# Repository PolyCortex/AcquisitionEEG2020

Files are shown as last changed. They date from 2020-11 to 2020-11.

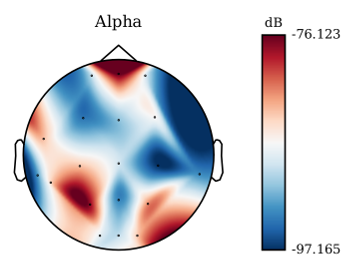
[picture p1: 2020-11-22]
software/gui/img/mne_head.png

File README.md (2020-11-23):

<h1 align="center">
  <br>
  Acquisition board 2020
  <br>
  Acquisition board 2020
  <br>
</h1>

<h4 align="center">A 4-channels biosignal acquisition pipeline.</h4>
<p align="center">
  <a href="http://polycortex.polymtl.ca/">
    
  </a>
 </p>

<p align="center">
  <a href="#key-features">Key Features</a> •
  <a href="#how-it-works">How It Works</a> •
  <a href="#project-structure">Project Structure</a> •
  <a href="#learn-more">Learn more</a> •
  <a href="#learn-more">About us</a>
</p>

---

The project contained in this repository is a 4-channel prototype board produced in the development of a PCB to acquire EEG signals. It contains an instrumentation amplifier, a notch filter and an anti aliasing filter. It is designed to be sampled either in a lab with the help of an oscilloscope or with a computer through a Teensy 3.2 microcontroller development board. As well, a signal visualization software can analyze the signal coming from this board.

**Disclaimer:** This prototype board does not work to sample EEG signals and was never intended as such. It was meant to be a platform used to test designs of filtering and amplification circuits, which we would have integrated into a true production PCB. However, our development cycle was slowed down due to the pandemic and we had to plan the release of the production version of the board for April 2021 instead. Even though we did not finish the project, we still wanted to show our progress and so we submit this prototype for the NeuroTechX 2020 Fixed Challenge.

## Key features

- A PCB which amplifies the signals and filters them through an analog acquisition pipeline.
- A realtime data acquisition software that can records, save, perform machine learning and neuroscience experiments.

## How it works

### Acquisition

The board includes four channels and so five electrodes should be placed on the patient's head: one per channel and a fifth reference electrode. The reference electrode is clipped at the patient's ear and voltages from the channel electrodes are measured against it.

### Signal processing

The full processing pipeline for EEG includes and instrumentation amplifier, which the measurement of extremely small EEG voltages. The pipeline also includes a high pass filter, a notch filter and a low pass filter which each eliminate different types of noise from the signal. 

### Data Transmission

After having been processed, the data is digitized by a microcontroller's Analog to Digital Converter (ADC) and sent to a computer.
Data from the board is received on the computer via one of its USB serial port. 

### Real-time visualization

The realtime visualization software can read the flow of data coming from the serial port and plot the signal on every channel in realtime. It can also show the data in the frequency domain using spectral, spectrogram and power band reprensentations.

### Data recording

All the raw data coming from the board can then be saved in a csv file for subsequent use.

## Project Structure

- The `cad/` folder contains files used to make the PCBs. The prototype board is under `cad/prototype-board/`. Two supply prototypes are included under `cad/supply-analog/` and `cad/supply-digital/`.
- The `components/` folder contains the datasheets for important components.
- The `simulations/` folder contains ltspice simulations for the elements of the analog processing pipeline.
- The `software/` folder contains everything that is linked to software. The computer software for digital signal processing and realtime visualization is under `software/gui/`. Check it out for more information about it. The microcontroller software for sampling the analog signals and to stream them to the computer is under  `software/teensy-code/`.

## Learn more

You can read more about the technical aspect of the prototype board, and of the planned production board in this
[wiki](https://github.com/PolyCortex/AcquisitionEEG2020/wiki).

## About us

[PolyCortex](http://polycortex.polymtl.ca/) is a student club based at [Polytechnique Montreal](https://www.polymtl.ca/).

The goal of PolyCortex is to develop expertise in neuroscience and engineering to solve neuroengineering problems. This field aims to create technological solutions dedicated to the search for innovative solutions to neuroscience problems.

To do this, we recommend the use of solutions revolving around the design of brain-machine interface devices, the implementation of embedded systems, the use of machine learning and signal processing techniques.

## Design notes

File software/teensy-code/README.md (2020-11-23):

# Acquisition 2020 Teensy code

## How it works

1. Starts four analog sampling channels and serial communication.
2. Starts a timer
3. After 5000 us have passed (200 Hz sample rate), the timer is reset, the four channels are sampled and the data is pushed through the serial interface.

## Getting started

In order to install the software on the Teensy, you need to download the arduino software, its teensy bridge and to connect the Teensy to the computer via USB.

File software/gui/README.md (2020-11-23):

# Acquisition 2020 GUI

Acquisition Software in action

This software is a new iteration of the software that was used for last year's Acquisition project. The major changes introduced by this new version are bug fixes, compatibility with our new acquisition board, changes to the UI, as well as some performance optimizations.

## Key features

- Connect itself to our custom Acquisition board, OpenBCI Cyton board, Muse headband and to a synthetic data stream;
- Multiple realtime signal processing visualizations such as time series, fourier transform, spectrogram, power band, etc;
- Records data and save it to a csv file format;
- Automatic Machine learning classification feature using a custom neural net;
- Tools make your ERP experiences easier.
- Dark mode! 🌙

## Getting started

In order to install the GUI software, please follow these instructions.

### Prerequisites

- Install Python 3.8.
  - Make sure that the "Python38\Scripts" folder is added to your environnment path varible on Windows in order to use pip and hupper without any issue.

### Setup

Create a new virtual environment to isolate Python packages.

> python -m venv .venv

Activate your virtual environment. This step will need to be done everytime you re-open your terminal.

- Linux/macOS:

> source .venv/bin/activate

- Windows:

> .\.venv\Scripts\activate.bat

Install the required dependencies.

> pip install -r requirements.txt

### Configuration for PCB communication

In order to communicate with the PCB, you will need to specify the serial port that will handle the communication. To do so, go to `generate_signal/from_pcb.py` and change the constant value `BAUDRATE` for the baudrate used on the MCU and `SERIAL_PORT` to the port used on your machine.

### Run

Finally, you can start te GUI using

> python main.py

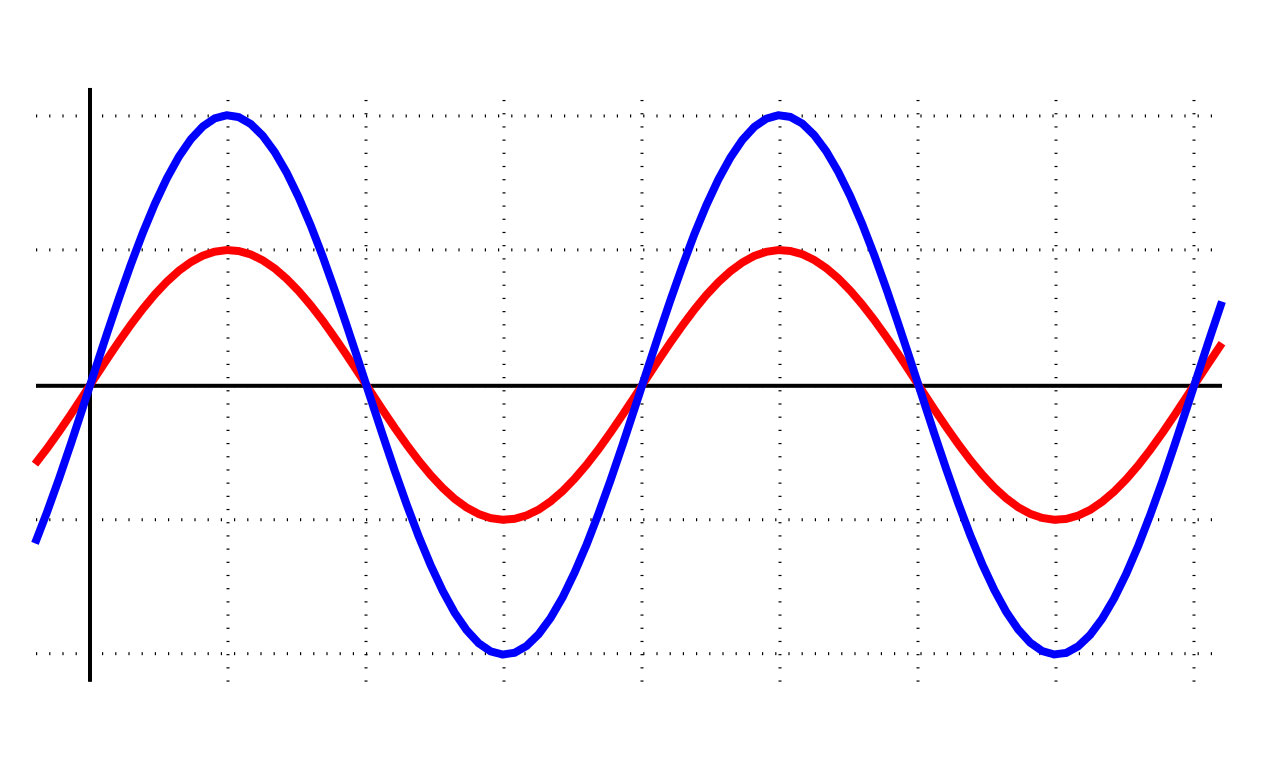
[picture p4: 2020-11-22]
software/gui/img/sinus.png

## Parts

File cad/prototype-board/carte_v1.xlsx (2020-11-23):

Id | Designator | Package | Quantity | Designation | Supplier and ref | Column1 | _1
1 | PS101 | Linear_DE14MA_manual_soldering | 1 | LT3032-5 | Analog Devices Inc. LT3032EDE-5#PBF
2 | BAT101,BAT102 | Battery_Holder_9V_BC9VPC-ND | 2 | BC9VPC | MPD (Memory Protection Devices) BC9VPC
3 | C101,C102,C103,C104,C201,C202,C203,C204,C301,C302,C303,C304,C401,C402,C403,C404,C501,C502,C503,C504,C601,C602,C603,C604,C605,C606,C607,C608,C701,C702,C703,C704,C705,C706,C707,C708,C801,C802,C803,C804,C805,C806,C807,C808,C901,C902,C903,C904,C905,C906,C907,C908,C1001,C1002,C1003,C1004,C1005,C1006,C1101,C1102,C1103,C1104,C1105,C1106,C1201,C1202,C1203,C1204,C1205,C1206,C1301,C1302,C1303,C1304,C1305,C1306 | C_0805_2012Metric_Pad1.15x1.40mm_HandSolder | 76 | 0.1uF
4 | C105,C106,C109,C110 | C_0805_2012Metric_Pad1.15x1.40mm_HandSolder | 4 | 10uF
5 | C107,C108 | C_0805_2012Metric_Pad1.15x1.40mm_HandSolder | 2 | 0.01uF
6 | C1007,C1107,C1207,C1307 | C_0805_2012Metric_Pad1.15x1.40mm_HandSolder | 4 | 0.015uF
7 | J101 | PinHeader_1x05_P2.54mm_Vertical | 1 | INPUTS
8 | J102 | PinHeader_1x05_P2.54mm_Vertical | 1 | POST_INSTR
9 | J103 | PinHeader_1x05_P2.54mm_Vertical | 1 | POST_NOTCH
10 | J104 | PinHeader_1x05_P2.54mm_Vertical | 1 | OUTPUTS
11 | R101,R201,R301,R401,R501 | R_0805_2012Metric_Pad1.15x1.40mm_HandSolder | 5 | 1k
12 | R102,R103,R104,R202,R203,R204,R302,R303,R304,R402,R403,R404,R502,R503,R504 | R_0805_2012Metric_Pad1.15x1.40mm_HandSolder | 15 | 1M | ±0.1%
13 | R601,R603,R701,R703,R801,R803,R901,R903 | R_0805_2012Metric_Pad1.15x1.40mm_HandSolder | 8 | 26.1k
14 | R602,R605,R702,R705,R802,R805,R902,R905,R1005,R1105,R1205,R1305 | R_0805_2012Metric_Pad1.15x1.40mm_HandSolder | 12 | 10k
15 | R604,R704,R804,R904 | R_0805_2012Metric_Pad1.15x1.40mm_HandSolder | 4 | 422
16 | R1001,R1101,R1201,R1301 | R_0805_2012Metric_Pad1.15x1.40mm_HandSolder | 4 | 1.8k
17 | R1002,R1102,R1202,R1302 | R_0805_2012Metric_Pad1.15x1.40mm_HandSolder | 4 | 5.1k
18 | R1003,R1103,R1203,R1303 | R_0805_2012Metric_Pad1.15x1.40mm_HandSolder | 4 | 3k
19 | R1004,R1104,R1204,R1304 | R_0805_2012Metric_Pad1.15x1.40mm_HandSolder | 4 | 249
20 | RV601,RV701,RV801,RV901 | Potentiometer_Bourns_TC33X_Vertical | 4 | R_POT_TRIM_US | Bourns Inc. TC33X-2-502E TRIMMER 5K OHM
21 | U101,U201,U301,U401,U501,U601,U701,U801,U901,U1001,U1101,U1201,U1301 | VSSOP-8_3.0x3.0mm_P0.65mm_manual_soldering | 13 | OPA2202 | Texas Instruments OPA2202IDGKR

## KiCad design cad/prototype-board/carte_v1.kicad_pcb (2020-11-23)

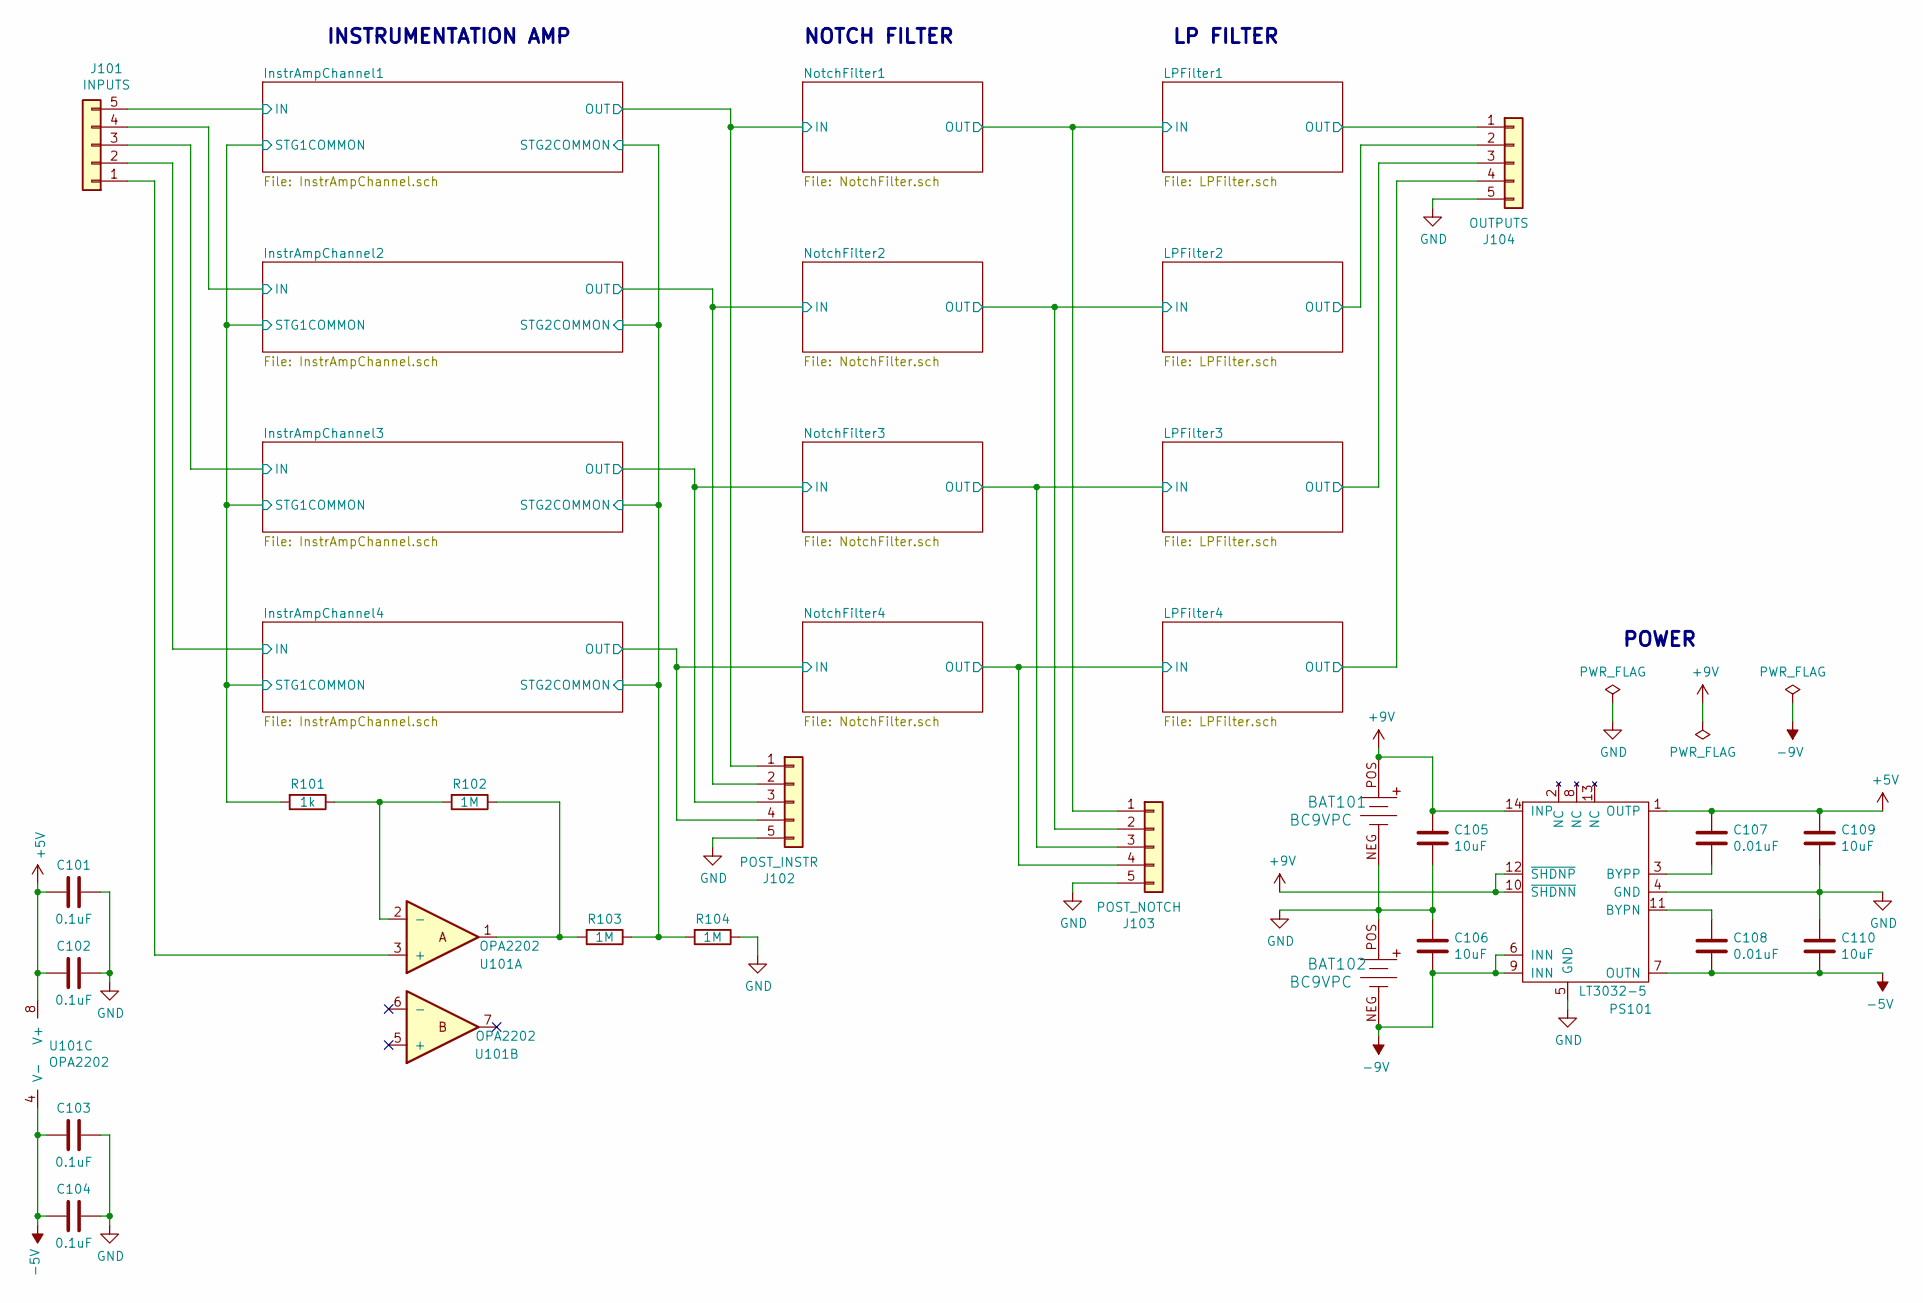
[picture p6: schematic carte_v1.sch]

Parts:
BAT101, BAT102: BC9VPC; Battery_Holder_9V_BC9VPC-ND; MPN BC9VPC; Digi-Key_PN BC9VPC-ND
C101, C102, C103, C104: 0.1uF; C_0805_2012Metric_Pad1.15x1.40mm_HandSolder
C105, C106, C109, C110: 10uF; C_0805_2012Metric_Pad1.15x1.40mm_HandSolder
C107, C108: 0.01uF; C_0805_2012Metric_Pad1.15x1.40mm_HandSolder
J101: INPUTS; PinHeader_1x05_P2.54mm_Vertical
J102: POST_INSTR; PinHeader_1x05_P2.54mm_Vertical
J103: POST_NOTCH; PinHeader_1x05_P2.54mm_Vertical
J104: OUTPUTS; PinHeader_1x05_P2.54mm_Vertical
PS101: LT3032-5; Linear_DE14MA_manual_soldering
R101: 1k; R_0805_2012Metric_Pad1.15x1.40mm_HandSolder
R102, R103, R104: 1M; R_0805_2012Metric_Pad1.15x1.40mm_HandSolder
U101: OPA2202; VSSOP-8_3.0x3.0mm_P0.65mm_manual_soldering

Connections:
+5V: C101.2, C102.2, C107.1, C109.1, PS101.1 (OUTP), U101.8 (V+); also elsewhere on the board
+9V: BAT101.POS, C105.1, PS101.10 (~SHDNN), PS101.12 (~SHDNP), PS101.14 (INP)
-5V: C103.2, C104.2, C108.2, C110.2, PS101.7 (OUTN), U101.4 (V-); also elsewhere on the board
-9V: BAT102.NEG, C106.2, PS101.6 (INN), PS101.9 (INN)
/InstrAmpChannel1/IN: J101.5; also elsewhere on the board
/InstrAmpChannel1/STG1COMMON: R101.2; also elsewhere on the board
/InstrAmpChannel1/STG2COMMON: R103.1, R104.2; also elsewhere on the board
/InstrAmpChannel2/IN: J101.4; also elsewhere on the board
/InstrAmpChannel3/IN: J101.3; also elsewhere on the board
/InstrAmpChannel4/IN: J101.2; also elsewhere on the board
/LPFilter1/IN: J103.1; also elsewhere on the board
/LPFilter1/OUT: J104.1; also elsewhere on the board
/LPFilter2/IN: J103.2; also elsewhere on the board
/LPFilter2/OUT: J104.2; also elsewhere on the board
/LPFilter3/IN: J103.3; also elsewhere on the board
/LPFilter3/OUT: J104.3; also elsewhere on the board
/LPFilter4/IN: J103.4; also elsewhere on the board
/LPFilter4/OUT: J104.4; also elsewhere on the board
/NotchFilter1/IN: J102.1; also elsewhere on the board
/NotchFilter2/IN: J102.2; also elsewhere on the board
/NotchFilter3/IN: J102.3; also elsewhere on the board
/NotchFilter4/IN: J102.4; also elsewhere on the board
GND: BAT101.NEG, BAT102.POS, C101.1, C102.1, C103.1, C104.1, C105.2, C106.1, C109.2, C110.1, J102.5, J103.5, J104.5, PS101.4 (GND), PS101.5 (GND), R104.1; also elsewhere on the board
unnamed: C107.2, PS101.3 (BYPP)
unnamed: C108.1, PS101.11 (BYPN)
unnamed: J101.1, U101.3 (+)
unnamed: R101.1, R102.2, U101.2 (-)
unnamed: R102.1, R103.2, U101.1

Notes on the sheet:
POWER
INSTRUMENTATION AMP
NOTCH FILTER
LP FILTER

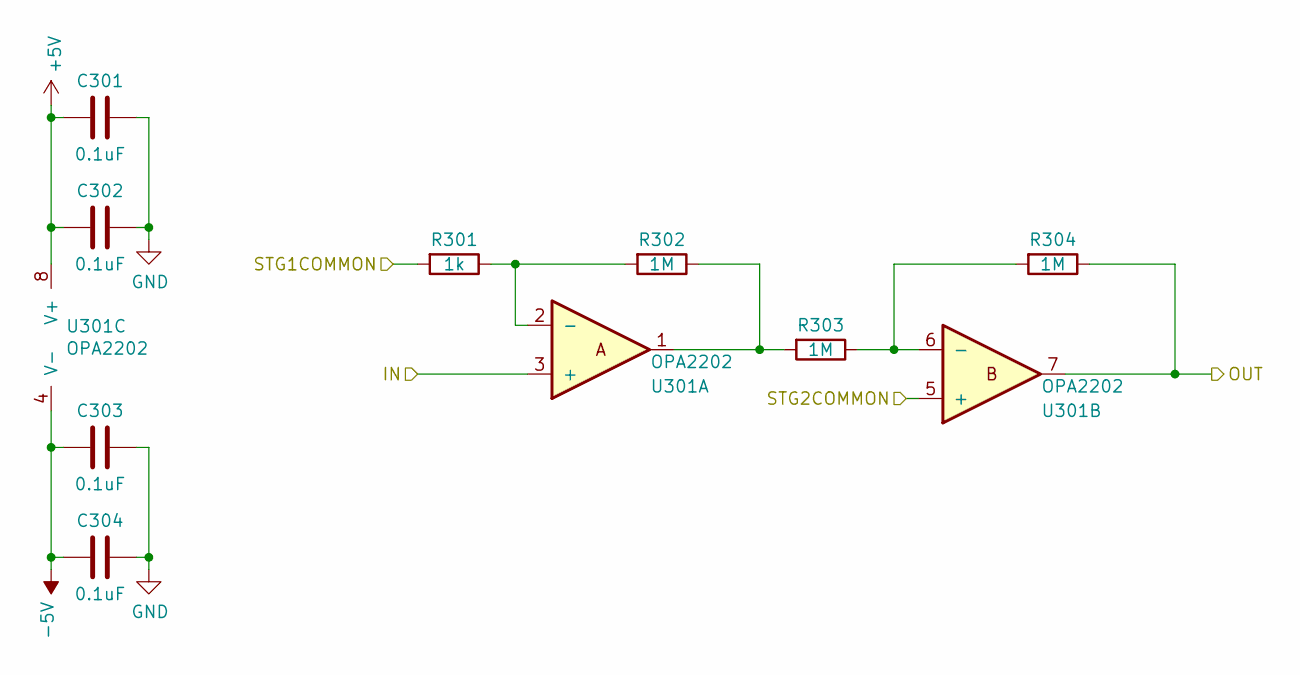
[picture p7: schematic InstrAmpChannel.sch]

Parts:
C201, C202, C203, C204: 0.1uF; C_0805_2012Metric_Pad1.15x1.40mm_HandSolder
R201: 1k; R_0805_2012Metric_Pad1.15x1.40mm_HandSolder
R202, R203, R204: 1M; R_0805_2012Metric_Pad1.15x1.40mm_HandSolder
U201: OPA2202; VSSOP-8_3.0x3.0mm_P0.65mm_manual_soldering

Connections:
+5V: C201.2, C202.2, U201.8 (V+); also elsewhere on the board
-5V: C203.2, C204.2, U201.4 (V-); also elsewhere on the board
/InstrAmpChannel1/IN: U201.3 (+); also elsewhere on the board
/InstrAmpChannel1/STG1COMMON: R201.2; also elsewhere on the board
/InstrAmpChannel1/STG2COMMON: U201.5 (+); also elsewhere on the board
/NotchFilter1/IN: R204.1, U201.7; also elsewhere on the board
GND: C201.1, C202.1, C203.1, C204.1; also elsewhere on the board
unnamed: R201.1, R202.2, U201.2 (-)
unnamed: R202.1, R203.2, U201.1
unnamed: R203.1, R204.2, U201.6 (-)

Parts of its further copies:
C301, C302, C303, C304, C401, C402, C403, C404, C501, C502, C503, C504: 0.1uF; C_0805_2012Metric_Pad1.15x1.40mm_HandSolder
R301, R401, R501: 1k; R_0805_2012Metric_Pad1.15x1.40mm_HandSolder
R302, R303, R304, R402, R403, R404, R502, R503, R504: 1M; R_0805_2012Metric_Pad1.15x1.40mm_HandSolder
U301, U401, U501: OPA2202; VSSOP-8_3.0x3.0mm_P0.65mm_manual_soldering

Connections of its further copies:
+5V: C301.2, C302.2, C401.2, C402.2, C501.2, C502.2, U301.8 (V+), U401.8 (V+), U501.8 (V+); also elsewhere on the board
-5V: C303.2, C304.2, C403.2, C404.2, C503.2, C504.2, U301.4 (V-), U401.4 (V-), U501.4 (V-); also elsewhere on the board
/InstrAmpChannel1/STG1COMMON: R301.2, R401.2, R501.2; also elsewhere on the board
/InstrAmpChannel1/STG2COMMON: U301.5 (+), U401.5 (+), U501.5 (+); also elsewhere on the board
/InstrAmpChannel2/IN: U301.3 (+); also elsewhere on the board
/InstrAmpChannel3/IN: U401.3 (+); also elsewhere on the board
/InstrAmpChannel4/IN: U501.3 (+); also elsewhere on the board
/NotchFilter2/IN: R304.1, U301.7; also elsewhere on the board
/NotchFilter3/IN: R404.1, U401.7; also elsewhere on the board
/NotchFilter4/IN: R504.1, U501.7; also elsewhere on the board
GND: C301.1, C302.1, C303.1, C304.1, C401.1, C402.1, C403.1, C404.1, C501.1, C502.1, C503.1, C504.1; also elsewhere on the board
unnamed: R301.1, R302.2, U301.2 (-)
unnamed: R302.1, R303.2, U301.1
unnamed: R303.1, R304.2, U301.6 (-)
unnamed: R401.1, R402.2, U401.2 (-)
unnamed: R402.1, R403.2, U401.1
unnamed: R403.1, R404.2, U401.6 (-)
unnamed: R501.1, R502.2, U501.2 (-)
unnamed: R502.1, R503.2, U501.1
unnamed: R503.1, R504.2, U501.6 (-)

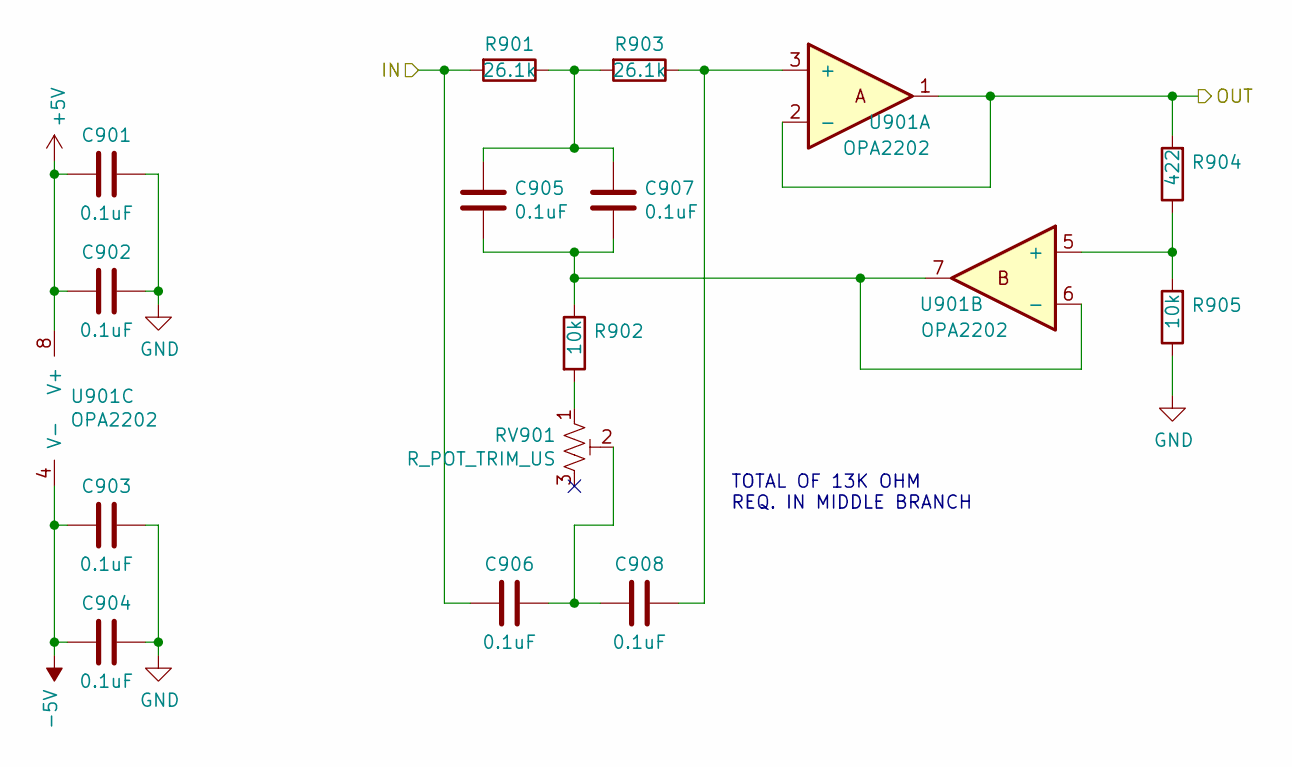
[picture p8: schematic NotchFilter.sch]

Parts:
C601, C602, C603, C604, C605, C606, C607, C608: 0.1uF; C_0805_2012Metric_Pad1.15x1.40mm_HandSolder
R601, R603: 26.1k; R_0805_2012Metric_Pad1.15x1.40mm_HandSolder
R602, R605: 10k; R_0805_2012Metric_Pad1.15x1.40mm_HandSolder
R604: 422; R_0805_2012Metric_Pad1.15x1.40mm_HandSolder
RV601: R_POT_TRIM_US; Potentiometer_Bourns_TC33X_Vertical
U601: OPA2202; VSSOP-8_3.0x3.0mm_P0.65mm_manual_soldering

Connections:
+5V: C601.2, C602.2, U601.8 (V+); also elsewhere on the board
-5V: C603.2, C604.2, U601.4 (V-); also elsewhere on the board
/LPFilter1/IN: R604.2, U601.1, U601.2 (-); also elsewhere on the board
/NotchFilter1/IN: C606.2, R601.2; also elsewhere on the board
GND: C601.1, C602.1, C603.1, C604.1, R605.1; also elsewhere on the board
unnamed: C605.1, C607.1, R601.1, R603.2
unnamed: C605.2, C607.2, R602.1, U601.6 (-), U601.7
unnamed: C606.1, C608.2, RV601.2
unnamed: C608.1, R603.1, U601.3 (+)
unnamed: R602.2, RV601.1
unnamed: R604.1, R605.2, U601.5 (+)

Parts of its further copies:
C701, C702, C703, C704, C705, C706, C707, C708, C801, C802, C803, C804, C805, C806, C807, C808, C901, C902, C903, C904, C905, C906, C907, C908: 0.1uF; C_0805_2012Metric_Pad1.15x1.40mm_HandSolder
R701, R703, R801, R803, R901, R903: 26.1k; R_0805_2012Metric_Pad1.15x1.40mm_HandSolder
R702, R705, R802, R805, R902, R905: 10k; R_0805_2012Metric_Pad1.15x1.40mm_HandSolder
R704, R804, R904: 422; R_0805_2012Metric_Pad1.15x1.40mm_HandSolder
RV701, RV801, RV901: R_POT_TRIM_US; Potentiometer_Bourns_TC33X_Vertical
U701, U801, U901: OPA2202; VSSOP-8_3.0x3.0mm_P0.65mm_manual_soldering

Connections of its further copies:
+5V: C701.2, C702.2, C801.2, C802.2, C901.2, C902.2, U701.8 (V+), U801.8 (V+), U901.8 (V+); also elsewhere on the board
-5V: C703.2, C704.2, C803.2, C804.2, C903.2, C904.2, U701.4 (V-), U801.4 (V-), U901.4 (V-); also elsewhere on the board
/LPFilter2/IN: R704.2, U701.1, U701.2 (-); also elsewhere on the board
/LPFilter3/IN: R804.2, U801.1, U801.2 (-); also elsewhere on the board
/LPFilter4/IN: R904.2, U901.1, U901.2 (-); also elsewhere on the board
/NotchFilter2/IN: C706.2, R701.2; also elsewhere on the board
/NotchFilter3/IN: C806.2, R801.2; also elsewhere on the board
/NotchFilter4/IN: C906.2, R901.2; also elsewhere on the board
GND: C701.1, C702.1, C703.1, C704.1, C801.1, C802.1, C803.1, C804.1, C901.1, C902.1, C903.1, C904.1, R705.1, R805.1, R905.1; also elsewhere on the board
unnamed: C705.1, C707.1, R701.1, R703.2
unnamed: C705.2, C707.2, R702.1, U701.6 (-), U701.7
unnamed: C706.1, C708.2, RV701.2
unnamed: C708.1, R703.1, U701.3 (+)
unnamed: C805.1, C807.1, R801.1, R803.2
unnamed: C805.2, C807.2, R802.1, U801.6 (-), U801.7
unnamed: C806.1, C808.2, RV801.2
unnamed: C808.1, R803.1, U801.3 (+)
unnamed: C905.1, C907.1, R901.1, R903.2
unnamed: C905.2, C907.2, R902.1, U901.6 (-), U901.7
unnamed: C906.1, C908.2, RV901.2
unnamed: C908.1, R903.1, U901.3 (+)
unnamed: R702.2, RV701.1
unnamed: R704.1, R705.2, U701.5 (+)
unnamed: R802.2, RV801.1
unnamed: R804.1, R805.2, U801.5 (+)
unnamed: R902.2, RV901.1
unnamed: R904.1, R905.2, U901.5 (+)

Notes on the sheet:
TOTAL OF 13K OHM REQ. IN MIDDLE BRANCH

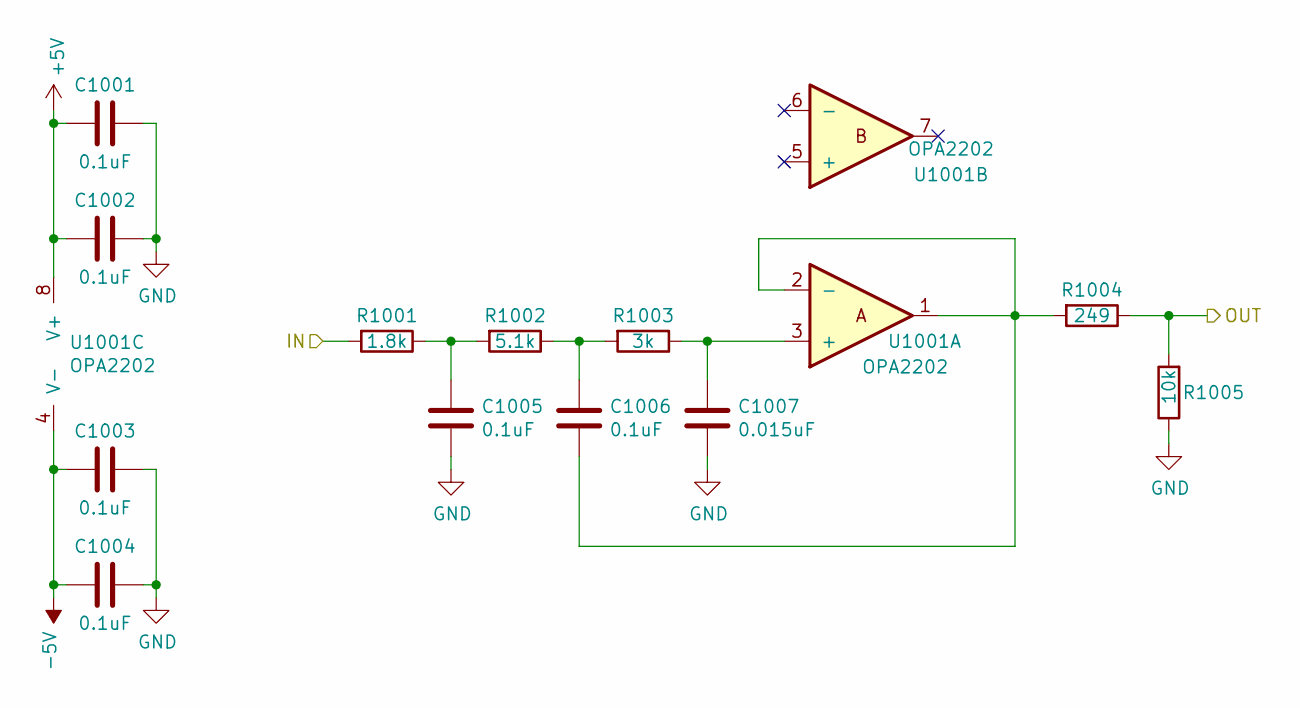
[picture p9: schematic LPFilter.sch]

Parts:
C1001, C1002, C1003, C1004, C1005, C1006: 0.1uF; C_0805_2012Metric_Pad1.15x1.40mm_HandSolder
C1007: 0.015uF; C_0805_2012Metric_Pad1.15x1.40mm_HandSolder
R1001: 1.8k; R_0805_2012Metric_Pad1.15x1.40mm_HandSolder
R1002: 5.1k; R_0805_2012Metric_Pad1.15x1.40mm_HandSolder
R1003: 3k; R_0805_2012Metric_Pad1.15x1.40mm_HandSolder
R1004: 249; R_0805_2012Metric_Pad1.15x1.40mm_HandSolder
R1005: 10k; R_0805_2012Metric_Pad1.15x1.40mm_HandSolder
U1001: OPA2202; VSSOP-8_3.0x3.0mm_P0.65mm_manual_soldering

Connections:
+5V: C1001.2, C1002.2, U1001.8 (V+); also elsewhere on the board
-5V: C1003.2, C1004.2, U1001.4 (V-); also elsewhere on the board
/LPFilter1/IN: R1001.2; also elsewhere on the board
/LPFilter1/OUT: R1004.1, R1005.2; also elsewhere on the board
GND: C1001.1, C1002.1, C1003.1, C1004.1, C1005.2, C1007.2, R1005.1; also elsewhere on the board
unnamed: C1005.1, R1001.1, R1002.2
unnamed: C1006.1, R1002.1, R1003.2
unnamed: C1006.2, R1004.2, U1001.1, U1001.2 (-)
unnamed: C1007.1, R1003.1, U1001.3 (+)

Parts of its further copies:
C1101, C1102, C1103, C1104, C1105, C1106, C1201, C1202, C1203, C1204, C1205, C1206, C1301, C1302, C1303, C1304, C1305, C1306: 0.1uF; C_0805_2012Metric_Pad1.15x1.40mm_HandSolder
C1107, C1207, C1307: 0.015uF; C_0805_2012Metric_Pad1.15x1.40mm_HandSolder
R1101, R1201, R1301: 1.8k; R_0805_2012Metric_Pad1.15x1.40mm_HandSolder
R1102, R1202, R1302: 5.1k; R_0805_2012Metric_Pad1.15x1.40mm_HandSolder
R1103, R1203, R1303: 3k; R_0805_2012Metric_Pad1.15x1.40mm_HandSolder
R1104, R1204, R1304: 249; R_0805_2012Metric_Pad1.15x1.40mm_HandSolder
R1105, R1205, R1305: 10k; R_0805_2012Metric_Pad1.15x1.40mm_HandSolder
U1101, U1201, U1301: OPA2202; VSSOP-8_3.0x3.0mm_P0.65mm_manual_soldering

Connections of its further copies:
+5V: C1101.2, C1102.2, C1201.2, C1202.2, C1301.2, C1302.2, U1101.8 (V+), U1201.8 (V+), U1301.8 (V+); also elsewhere on the board
-5V: C1103.2, C1104.2, C1203.2, C1204.2, C1303.2, C1304.2, U1101.4 (V-), U1201.4 (V-), U1301.4 (V-); also elsewhere on the board
/LPFilter2/IN: R1101.2; also elsewhere on the board
/LPFilter2/OUT: R1104.1, R1105.2; also elsewhere on the board
/LPFilter3/IN: R1201.2; also elsewhere on the board
/LPFilter3/OUT: R1204.1, R1205.2; also elsewhere on the board
/LPFilter4/IN: R1301.2; also elsewhere on the board
/LPFilter4/OUT: R1304.1, R1305.2; also elsewhere on the board
GND: C1101.1, C1102.1, C1103.1, C1104.1, C1105.2, C1107.2, C1201.1, C1202.1, C1203.1, C1204.1, C1205.2, C1207.2, C1301.1, C1302.1, C1303.1, C1304.1, C1305.2, C1307.2, R1105.1, R1205.1, R1305.1; also elsewhere on the board
unnamed: C1105.1, R1101.1, R1102.2
unnamed: C1106.1, R1102.1, R1103.2
unnamed: C1106.2, R1104.2, U1101.1, U1101.2 (-)
unnamed: C1107.1, R1103.1, U1101.3 (+)
unnamed: C1205.1, R1201.1, R1202.2
unnamed: C1206.1, R1202.1, R1203.2
unnamed: C1206.2, R1204.2, U1201.1, U1201.2 (-)
unnamed: C1207.1, R1203.1, U1201.3 (+)
unnamed: C1305.1, R1301.1, R1302.2
unnamed: C1306.1, R1302.1, R1303.2
unnamed: C1306.2, R1304.2, U1301.1, U1301.2 (-)
unnamed: C1307.1, R1303.1, U1301.3 (+)

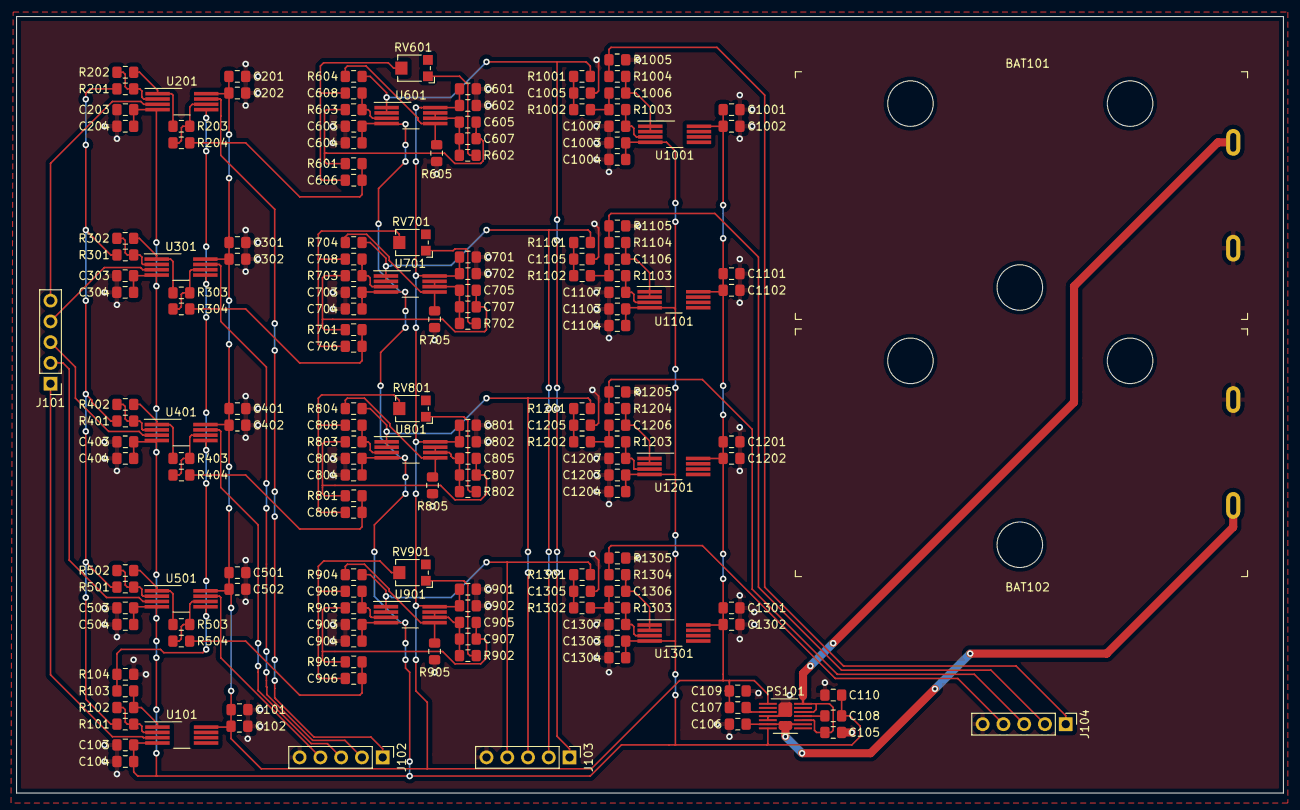
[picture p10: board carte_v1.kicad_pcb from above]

Board: 2 copper layers, 155.0 x 95.0 mm, 170 parts (0 on the bottom side), 80 nets.

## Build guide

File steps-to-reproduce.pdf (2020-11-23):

## Steps to Reproduce the Project

### 1. Install KICAD 2. Open the “prototype-board’ project in the “cad” folder of the GitHub

repository.
3. Use the schematics, BOM and gerber files to order copies of the PCB. Companies that manufacture PCBs include ALLPCB and JLCPCB.

### 4. Choose if you want to solder the board yourself or if you want the company to

do it. Be advised that if you want to solder the board yourself, you will need specialised equipment as the op amps are very small and the power supply chip does not have exposed pins.

### 5. If you chose to solder the board yourself, order the components in the BOM

provided by KICAD. If you chose to have the PCB manufacturing company solder the board for you, be sure to pay for the components at the same time as you pass the order for the board. This will allow them to order the components at the earliest and will cut down on manufacturing time.

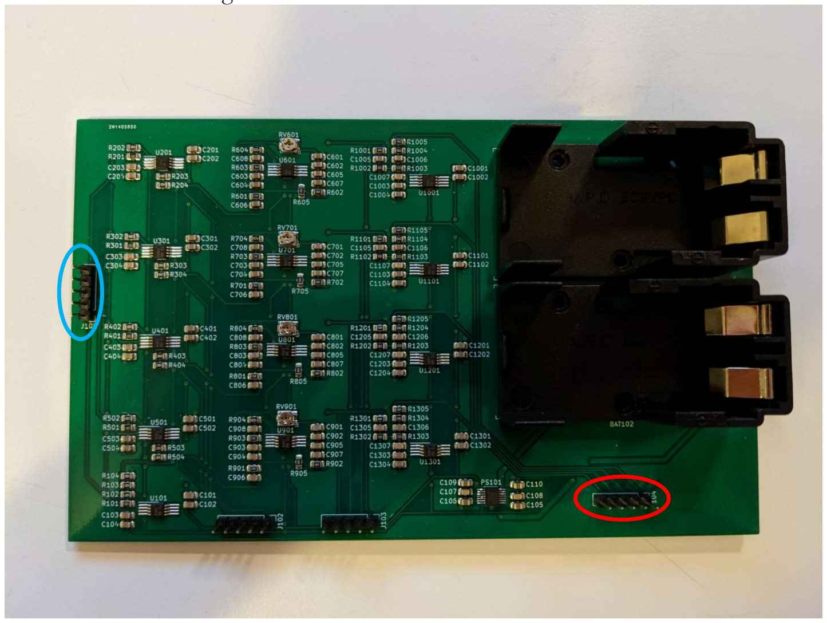
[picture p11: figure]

Figure 1: Prototype EEG Acquisition Board

### 6. Insert two 9v batteries in the battery holders 7. Connect the electrodes to the header pins circled in blue in figure 1 and the

Teensy 3.2, pins A0, A1, A2, A3 and GND to the header pins circled in red in figure 1.
8. Download the Arduino software and its teensy bridge.
9. Connect the teensy to your computer with a USB cable.

### 10. Program the teensy with the software in the “software/teensy-code” folder in

the GitHub repository

### 11. Use the README in the “software/gui” folder of the GitHub repository to

configure the environment and to use the visualization software.

### 12. Before using the board, you may want to test it. To do so, use a function

generator with a sinus signal at a 60 Hz frequency and an amplitude of 100 mV through a 1/1000 voltage divider. Connect the ground of the function generator to the reference electrode and the output of the voltage divider to any of the signal electrodes. There should be no output.

### 13. If you have an output, tweak the potentiometer associated with the channel in

use until the signal disappears.
14. To test the board, change the frequency of the function generator to 40 Hz.

### 15. The remaining pins on the prototype board can be used to sample the signal at

each step in the processing pipeline.

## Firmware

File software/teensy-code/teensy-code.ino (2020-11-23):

/*
 ______      _       _______                                 _               _
(_____ \    | |     (_______)             _                 (_)          _  | |
 _____) )__ | |_   _ _       ___   ____ _| |_ _____ _   _    _  ___    _| |_| |__  _____
|  ____/ _ \| | | | | |     / _ \ / ___|_   _) ___ ( \ / )  | |/___)  (_   _)  _ \| ___ |
| |   | |_| | | |_| | |____| |_| | |     | |_| ____|)   (   | |___ |    | |_| | | | ____|
|_|    \___/ \_)__  |\______)___/|_|      \__)_____|_/ \_)  |_(___/      \__)_| |_|_____)  (shit)
              (____/
*/

int ACH_1_pin = A0;
int ACH_2_pin = A1;
int ACH_3_pin = A2;
int ACH_4_pin = A3;

uint32_t ACH_1 = 0;
uint32_t ACH_2 = 0;
uint32_t ACH_3 = 0;
uint32_t ACH_4 = 0;

unsigned long start_usecs;

void setup() {
  Serial.begin(115200);
  start_usecs = micros();
}

void loop() {
  if (micros() - start_usecs > 5000){

    //reset start time
    start_usecs = micros();

    //read analog data
    ACH_1 = analogRead(ACH_1_pin);
    ACH_2 = analogRead(ACH_2_pin);
    ACH_3 = analogRead(ACH_3_pin);
    ACH_4 = analogRead(ACH_4_pin);

    //send the data over serial
    Serial.println(ACH_1);
    Serial.println(ACH_2);
    Serial.println(ACH_3);
    Serial.println(ACH_4);
    
  }
}
